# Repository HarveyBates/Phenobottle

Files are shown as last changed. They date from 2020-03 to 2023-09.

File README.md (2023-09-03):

Phenobottle

Phenobottle

---

### Description

An open-source Raspberry-Pi based photobioreactor for cultivating and assessing physiology (photosynthesis & productivity) in microscopic algae. The device can be used to cultivate both green algae and cyanobacteria while continuiously (and non-invasively) probing photosynthetic and growth phenotypes.

#### Publication

The device was published in [Algal Research in 2020](https://www.sciencedirect.com/science/article/abs/pii/S2211926420309735):

*The Phenobottle, an open-source photobioreactor platform for environmental simulation - Bates et al. 2020*



#### Future of The Phenobottle

The Phenobottle is currently being updated to version 0.2. This will feature several environmental controls that were not featured the original version (v0.1) of the device. Additonal environmental sensors will also feature in version 0.2 along with a graphical user interface (GUI). 

If you would like to learn more about the progress of this version please email: [harvey_bates@hotmail.com](harvey_bates@hotmail.com)

---

### [Live](https://youtu.be/7FyAfFrLizw) Preview

PhenobottleGIF (https://youtu.be/7FyAfFrLizw)

___

# Operating Manual

## Specifications

| Feature                                                      | Value / Description                                          |
| ------------------------------------------------------------ | ------------------------------------------------------------ |
| Growth light quality                                         | Red, green and blue (Adjustable). 8-bit individual adjustment for each channel. |
| Growth light intensity                                       | Up to 200 &mu;E (can be increased if needed).                |
| Mixing                                                       | Vertical mixing using magnetic stirrer (adjustable intensity) |
| Bubbling                                                     | Included bubbling motor (adjustable) or solenoid control for external supply of CO<sub>2</sub> |
| Main board                                                   | Raspberry Pi 3B+ (can accomidate the new 4 - 4B)             |
| Microcontroller                                              | Teensy 3.5/3.6 or Teensy 4.1 (3.6 Recommended)               |
| Actinic LED colors                                           | **Blue** 455 – 485 nm (466 nm), **Green** 517 – 555 nm (532 nm), **Orange** 583 – 600 nm (593 nm), **Red** 617 – 635 nm (626 nm). |
| Resolution of **optical density** and **chlorophyll fluorescence** measurments | 10 to 16-bit (adjustable)                                    |
| Sampling rate of fluorometer                                 | 8 &mu;s at 12-bits (can be overclocked)                      |
| Operating voltage                                            | 15 V 1.2 A (Barrel plug), 12 V 2 A (Barrel Plug) and a 5 V 2 A (MicroUSB) power supply |
| Data collection                                              | SQL Server and local .csv                                    |

## Downloading files from this repository

As the Phenobottle is being updated constantly, please download a released version of the device from the releases tab (located on the right hand side of the screen). This contains all the files needed to 3D-print and control Phenobottles as well as some information about the required materials and tools. 

If you wish to clone the main repository you may; however, as there are new versions of the Phenobottle in the works, the files may not work as planned.

## Python dependencies

A number of packages are included in the [Phenobottle_RaspberryPi.py](Phenobottle_RaspberryPi.py). Some of which are already installed on a Raspberry Pi and as such wont be discussed. Others need to be installed using the Raspberry Pi terminal before compiling, these include: 
### PyMySQL - For SQL connection
#### Terminal
```bash
pip3 install PyMySQL
```
#### Python
```python
import pymysql.cursors
```
This requires a Raspberry Pi to be configured as a dedicated SQL server. Information on how to do that can be found [here](https://pimylifeup.com/raspberry-pi-mysql/). It is recomended that you use a dedicated Raspberry Pi for the SQL server; however, you can use one of the Phenobottle's Raspberry Pi's as a server if you are limited.

### Adafruit_MotorHAT - For I2C communication with the [Adafruit-MotorHAT](https://www.adafruit.com/product/2348)
#### Terminal
```bash
git clone https://github.com/adafruit/Adafruit-Motor-HAT-Python-Library.git
cd Adafruit-Motor-HAT-Python-Library
python3 setup.py install
```
#### Python
```python
from Adafruit_MotorHAT import Adafruit_MotorHAT
```
Unfortunatly this package is depreciated; however, its still fine to use for the Phenobottle.

### Twilio - SMS messaging
#### Terminal
```bash
pip3 install twilio
```
#### Python
```python
from twilio.rest import Client
```
This package is not required if you do not want to recieve SMS updates. Twilio is a paid service that you must sign up for [here](https://www.twilio.com/). However, this is non-essential and the Phenobottle runs fine without this addition. This can be handy if you are away from The Phenobottle and need to know how the experiment is running. 

### pySerial - Serial (USB) communication with the microcontroller
#### Terminal
```bash
python3 -m pip install pyserial
```
#### Python
```python
import serial
```
Required for communication with the Teensy 3.6 microcontroller. Documentation on this package can be found [here](https://pyserial.readthedocs.io/en/latest/index.html). 

## Required setup in [Phenobottle_RaspberryPi.py](Phenobottle_RaspberryPi.py)
### Basic Setup
```python
PHENOBOTTLE_NUMBER = 3 # Arbitary number to differentiate between Phenobottles
INITIAL_OPTICAL_DENSITY = 888 # 12-bit value obtained by calibrating the optical density sensor
ARDUINO_FLUORESCENCE_REFERENCE = 3.3 # Teensy microntrollers have 2 analog reference values 1.1 and 3.3 
MIXING_SPEED = 32 # Mixing speed of the mixing motor (0 - 255)
BUBBLING_INTENSITY = 60 # Bubbling intensity of the bubbling motor (0 - 255)
LIGHT_INTENSITY = 220 # Overall light intensity of the grow lights (0 - 255) 
PERISTALTIC_SPEED = 160 # Speed of the peristaltic pump (0 - 255)
EXPERIMENT_START_TIME = "07:00:00" # Specify when the experiment should start 

ser = serial.Serial('/dev/ttyACM0', 115200) # Serial port and baud rate of Teensy 3.6 microcontroller
```
The `INITAL_OPTICAL_DENSITY` value is obtained by reading the raw value of optical density BEFORE adding microalgae to the flask. This can be acheived by writing "MeasureOpticalDensity" in the serial input of the Teensy 3.6 microcontroller (in the ArduinoIDE) or calling `Test.prelim_od()` in the python [file](Phenobottle_RaspberryPi.py). This is required to obtain a 100% transmission reading for which optical density measurments can be formulated from in the code. 

### SQL Setup
```python
connection = pymysql.connect(host='IP_ADDRESS', # IP address of Raspberry Pi SQL server
                             port=port_number, # Usually 3306
                             user='Username', # Username of phpmyadmin 
                             password='Password', # Password of phpmyadmin
                             db='Phenobottle No.%s' %PHENOBOTTLE_NUMBER, # Database name
                             charset='utf8mb4',
                             cursorclass=pymysql.cursors.DictCursor)
```
For a SQL server connection this command must be compiled. See [here](https://pypi.org/project/PyMySQL/) for some documentation related to PyMySQL. For the database name you can change this to whichever name you choose; however, here we have premaded databases in out SQL server named "Phenobottle No.1", "Phenobottle No.2" ..., so that the `PHENOBOTTLE_NUMBER` corresponds with the correct database. 

### Messaging Setup
```python
acc_sid = "Account SSID" # Accound SSID from Twilio
auth_token = "Account Token" # Accound token from Twilio
client = Client(acc_sid, auth_token)
from_number = "Twilio Phone Number" # Designated twilio phone number
to_number = "Mobile Phone Number" # Your phone number
```
As mentioned above, this part isn't really nessessary. However, information regarding the setup of SMS messaging can be found [here](https://www.twilio.com/).

## Experimental procedure
### Measurment Intervals
The Phenobottle is capable of measuring/controling environmental variables at described intervals. This is done through this set of commands:
```python
""" Here we can check if the current time in minutes is devisable by our required measuring interval in this case 10 minutes. This means every 10 minutes a routine (day or night) will be run."""
if datetime.datetime.now().minute % 10 == 0: 
    """ Here we can setup or morning (8:00) and night times (20:00)"""
    if Experiment.experiment_schedule(datetime.time(8, 00), datetime.time(20, 00)): 
        NOW = datetime.datetime.now()
        Experiment.day_routine() # Runs the day routine
    else:
        NOW = datetime.datetime.now() 
        Experiment.night_routine() # Runs the night routine
```
### Routines
The day and the night routine are idential except for the fact that during the night the LED grow lights are constantly switched OFF. 
```python
MotorsAndLights.light_on(None) # Turn on lights (daytime only) with desired color
MotorsAndLights.mixing_motor_on() # Mixing on at set speed
time.sleep(30) # Wait 30 seconds for mixing 

MotorsAndLights.mixing_motor_off() # Mixing off
MotorsAndLights.light_off() # Lights off to ensure no noise from PWM interferes with measurments
Sensors.measure_optical_density() # Measures optical density
Sensors.measure_fluorescence() # Measures fluorescence

MotorsAndLights.light_on(None) # Turn on lights (daytime only) with desired color
MotorsAndLights.peristaltic_motor_on() # Pump on to clear cuvette
Database.upload() # Upload to SQL server
Excel.upload() # Upload to local .csv file
time.sleep(20) # Wait for pump to clear cuvette 

MotorsAndLights.peristaltic_motor_off() # Stop pump
MotorsAndLights.bubbling_motor_on() # Bubble main culture flask on
MotorsAndLights.mixing_motor_on() # Mixing on to homogenate culture
time.sleep(30) # Wait 30 seconds for bubbling and mixing 

MotorsAndLights.bubbling_motor_off() # Bubbling off
MotorsAndLights.mixing_motor_off() # Mixing off
```
This procedure is completely customisable, i.e. methods can be swapped around and the length of certain processes such as the bubbling time can be increased easily. 

# [Teensy 3.6](https://www.pjrc.com/store/teensy36.html) Microcontroller 
Analog functions are carried out by a Teensy 3.6 microcontroller which is connected to the Rasberry Pi via a serial (USB) connection. These analog functions include the measurement of optical density (growth), temperture and chlorophyll fluorescence (photosynthesis). 

The Teensy microcontroller can be programed with the [Arduino IDE](https://www.arduino.cc/en/Main/Software) on the Raspberry Pi if the additional software provided by [PJRC](https://www.pjrc.com/) called [Teensyduino](https://www.pjrc.com/teensy/teensyduino.html) is installed. 

The Teensy [code](Phenobottle_Teensy.ino) is flashed to the Teensy board and doesn't need modifying as it acts as a slave to the Raspberry Pi. 

## Teensy Setup
```c++
void setup() {
  Serial.begin(115200); // Initalise serial communications at specific baud rate
  analogReadResolution(12); // Set the resolution of the microcontroller in bits
  set_reference_voltage(refVoltage); // Only applicable with a Teensy 3.6 (disable if using other microcontroller)
  ...
}
```
## Teensy Slave Setup
The Teensy is constantly checking if there is requests in its serial port from the Raspberry Pi. It does this via the main loop:
```c++
void loop(){
  if(Serial.available()){   
    command = Serial.readStringUntil('\n');
    if(command.equals("MeasureOpticalDensity") || command.equals("MOD")){
      measure_optical_density();
    }
    else if(command.equals("MeasureFluorescence") || command.equals("MF")){
      measure_fluorescence();
    }
    ...
}
```
For example, when a string containing ```"MeasureOpticalDensity"``` into the Teensy's serial port, the resulting function ```measure_optical_density()``` is carried out. This simple design makes it easy to add new requests from the Raspberry Pi [.py](Phenobottle_RaspberryPi.py) file and the Teensy [.ino](Phenobottle_Teensy.ino) file by adding a new `else if` statement to this loop. 

## Fluorescence Measurment
### Setup
The Teensy in its current configuration takes a one second measurement of chlorophyll fluorescence, this however, can be adjusted as described below. The first part is to create arrays of different sizes corresponding to the time between measurements of fluorescence. The one second measurement is comprised of over 2000 data points which are comprised of fast (microsecond timescales) and slow (millisecond timescales) measurments:
2. Micro - Comprised of microsecond measurments (~8 &mu;s between measurments) of a set amount
3. Milli - Comprised of millisecond measurements (~1 ms between measurements) of a set amount
```c++
// Setup arrays that hold fluorescence data
int microRead [1000];
int milliRead[1000];

// Setup arrays that hold timestamps that correspond to fluorescence values
float microTime[1000]; 
float milliTime[1000];
String command;

int microLength = 1000, milliLength = 1000; // Change these to match the size of the above arrays
```
### Read
The measurment procedure is as follows:
```c++
void measure_fluorescence() {
  set_reference_voltage(refVoltage); 
  digitalWrite(actinicPin, HIGH); // Turn on actinic LED
  long timer = micros(); // Start timer 
  ...
```
The measurment is carried out in two seperate parts (1) `microRead` and (2) `milliRead`. The `analogRead` values are stored in their respective arrays with corresponding timestamps in their own array.
```c++
  // Read microsecond fluorescence values and corresponding timestamps
  for (unsigned int i = 0; i < sizeof(microRead) / sizeof(int); i++) 
  {
    microRead[i] = analogRead(fluorescenceReadPin);
    microTime[i] = micros() - timer;
  }

  // Read millisecond fluorescence values and corresponding timestamps
  for (unsigned int i = 0; i < sizeof(milliRead) / sizeof(int); i++) 
  {
    milliRead[i] = analogRead(fluorescenceReadPin);
    milliTime[i] = micros() - timer;
    delay(1); // Delay ~ 1ms between aqusisitions
  }
  ...
```
Any processing (converting timestamps from `micros` to milliseconds) of the arrays after this measurment is carried out after the actinic LED is switched off. This speeds up the `analogRead` function as we only need to store array values while measuring. 

## Optical Density
Measurment of optical density is really simple. 
```c++
void measure_optical_density(){
  set_reference_voltage(refVoltage);
  digitalWrite(odEmitPin, HIGH); // Turn on emitting LED
  delay(500); // Slight delay to ensure emitting LED is stable
  int odMeasure = analogRead(odReadPin); // Read optical density
  Serial.println(odMeasure);
  digitalWrite(odEmitPin, LOW); // Turn off emitting LED
}
```

# Open-Source Licensing

The software in this work is licensed under GNU AFFERO GENERAL PUBLIC LICENSE
  Copyright (C) (2020)  (Harvey Bates)

  This program is free software: you can redistribute it and/or modify
  it under the terms of the GNU General Public License as published by
  the Free Software Foundation, either version 3 of the License, or
  (at your option) any later version.

  This program is distributed in the hope that it will be useful,
  but WITHOUT ANY WARRANTY; without even the implied warranty of
  MERCHANTABILITY or FITNESS FOR A PARTICULAR PURPOSE.  See the
  GNU General Public License for more details.

  You should have received a copy of the GNU General Public License
  along with this program.  If not, see <https://www.gnu.org/licenses/>

  For more information contact: harvey.bates@student.uts.edu.au



Hardware (3D Models, Electronic Schematics) in this work is licensed under a <a rel="license" href="http://creativecommons.org/licenses/by-sa/3.0/">Creative Commons Attribution-ShareAlike 3.0 Unported License</a>.

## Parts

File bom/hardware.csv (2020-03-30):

Item | Quantity | Supplier | Notes
Mainframe | 1 | 3D Print
Lid | 1 | 3D Print
Magnetic Motor Attachment | 1 | 3D Print
Culture Flask Cap | 1 | 3D Print
Circuit Board | 1 | JLCPCB or Other | Upload "Phenobottle_Circuit_Gerber" to JLCPCB
Mixing Motor | 1 | YM2716, Jaycar, Rydalmere, AUS
Bubbling Motor | 1 | Vacuum Pump 12V, Core-Electronics, Kotara, AUS
Peristaltic Motor | 1 | 50220, Makeblock, Shenzhen, China
Light Strips | ~50 cm | RGB LED Bare, Core-Electronics, Kotara, AUS
Raspberry Pi 3B+ | 1
Raspberry Pi Motor HAT | 1 | Adafruit
Teensy 3.6 | 1
Stacking Headers (8 Pin) | 12 | Dfrobot | To connect teensy to circuit board
USB to Micro-USB cable | 1 |  | To connect teensy to rpi. Shorter the better.
875 nm LED | 2 | SIR333-A, Everlight, New Taipei City, Taiwan
10 W LED (COB SMD Chip) | 1 | Ebay | 466 nm, 532 nm, 592 nm, 626 nm
Heat Sink for LED (Optional) | 1 |  | 20 mm x 20 mm
Wire (Red and Black) | 25 m | 0.12 mm guage | For connecting motors to Motor HAT
Silicone Tubing | 5 m | 310-0305, Gecko Optical, Joondalup, AUS5 | 5mm OD x 3 ID mm. Use this to connect all tubing and inside of peristaltic pump. Use Irrigation Joiners (see below)
Polystrene Spectrometer Cuvette | 1 | C5291, Sigma Aldrich, NSW, AUS | Cut the bottom off
Poly Irrigation Barbed 4mm Joiner T/off Pk10 | 1 | Pope | Stick these to bottom and top of poly cuvette
Selleys aquafix glue (Epoxy) | 1 | Selleys | Use this to glue the above (or a waterproof alternative
Selleys 5 minute (Epoxy) ultraclear | 1 | Selleys | Use this to glue other parts (LEDs, motor attachments etc.)
12 V 2 A power supply | 1 | 15DYS624, Ideal Power, Texas, AUS | To power motors through motor hat
DC barrel jack adaptor (Female) | 1 | Dfrobot | Use this to attach the 12v 2a power supply to the motor hat
15 V 1.2 A power supply | 1 | DYS618 | Plug this into the phenobottle circuit board dc plug
5 V 2.5 A power supply | 1 | Raspberry Pi | Use this to power the raspberry pi
695 nm longpass filter | 1 | Thorlabs, New Jersey, USA | For fluorometer (position infront of photodiode)
IR cut-off filter | 1 | IR Filter, Lilly Electronics, Q-BAIHE, Hubei Province, ROC | For fluorometer (position infront of emitting LED)
Falcon Flask (Culture Flask) | 1 | Falcon Flask, Corning, NY, USA
Nylon 5/32" OD | 30 | Any | Glued inside cap to attach silicone tubing to
Neudynium Magnets | 2 | Any | 5 mm OD x 2 mm W

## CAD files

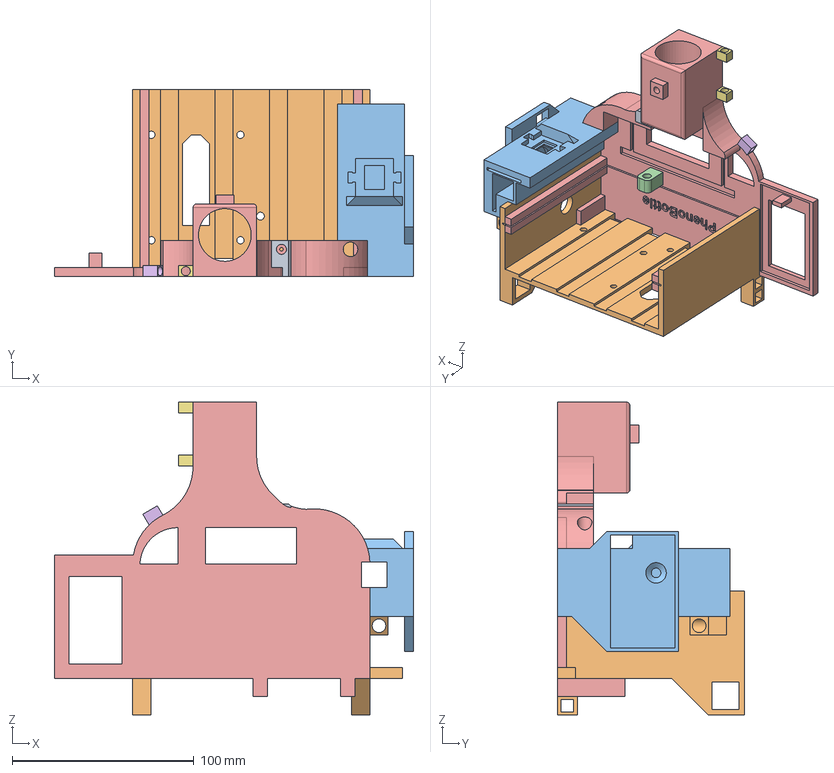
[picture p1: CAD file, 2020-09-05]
models/STEP Files/Phenobottle Main Frame.step
197.5 x 103.0 x 172.0 mm
OD Emitter Module
Light Enclosure
FluroHolder
OD Detector Module

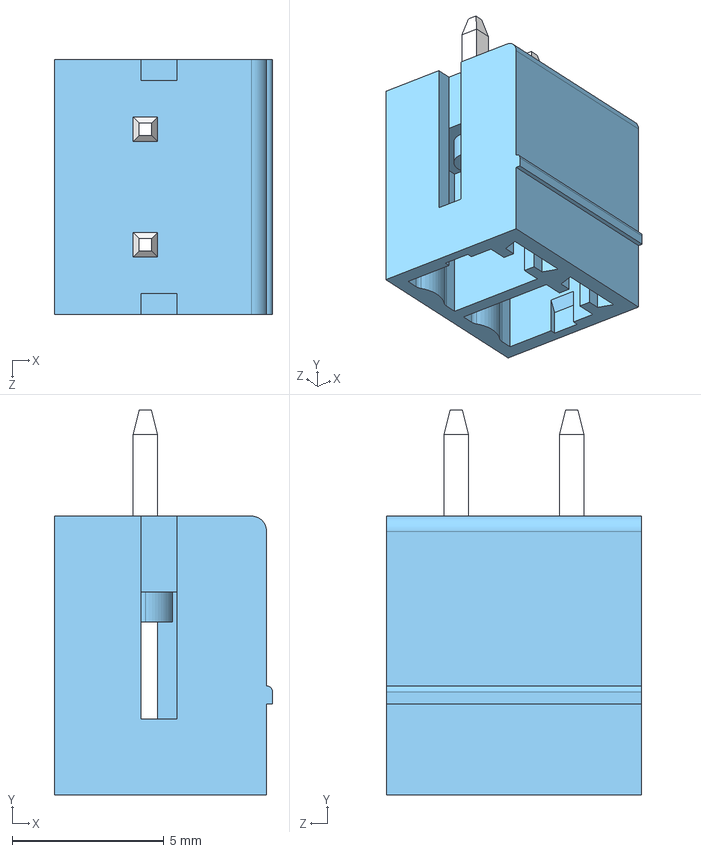
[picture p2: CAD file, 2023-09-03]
electronics/phenobottle/components/extern/3dmodels/connectors/TBP02R2-381-02BE.step
7.20 x 12.7 x 8.41 mm

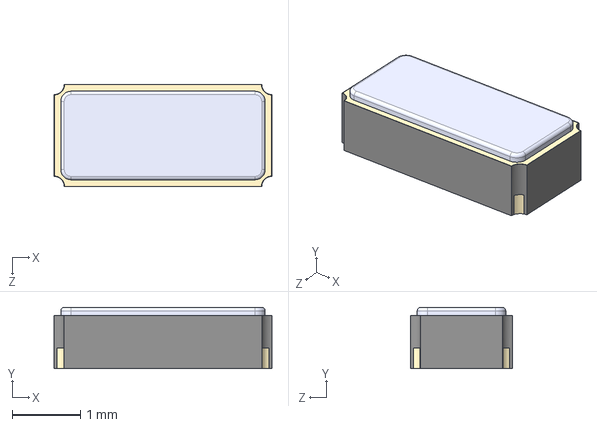
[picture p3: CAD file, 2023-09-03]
electronics/phenobottle/components/extern/3dmodels/crystals/ECS-.327-12.5-34R-C-TR.step
3.20 x 0.9 x 1.50 mm

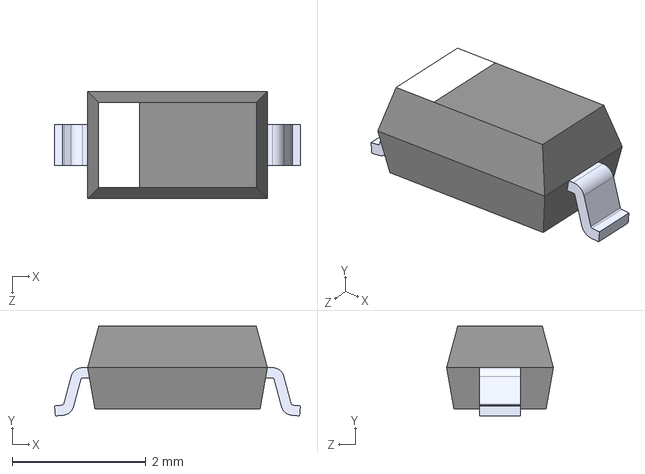
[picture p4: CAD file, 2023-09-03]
electronics/phenobottle/components/extern/3dmodels/diodes/MMSZ4700T1G.step
3.68 x 1.35 x 1.60 mm

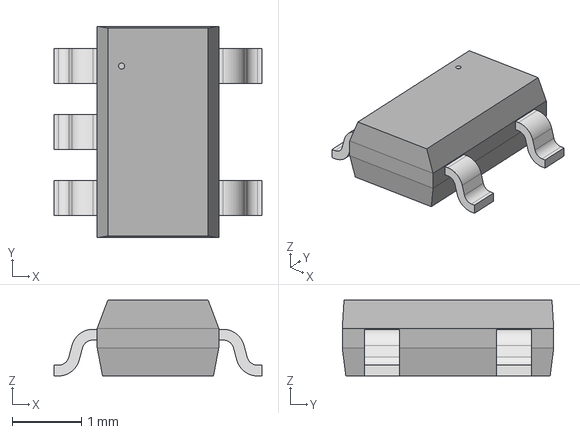
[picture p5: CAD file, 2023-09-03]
electronics/phenobottle/components/extern/3dmodels/op_amps/OPA328DBVR.step
3.00 x 3.05 x 1.09 mm

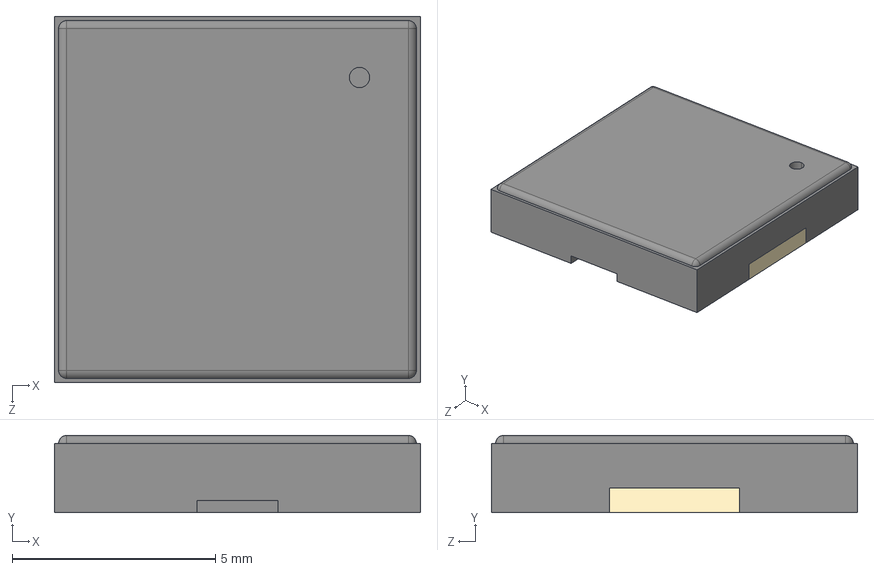
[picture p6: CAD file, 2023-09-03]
electronics/phenobottle/components/extern/3dmodels/piezo/PKMCS0909E4000-R1.step
9.00 x 1.90 x 9.00 mm

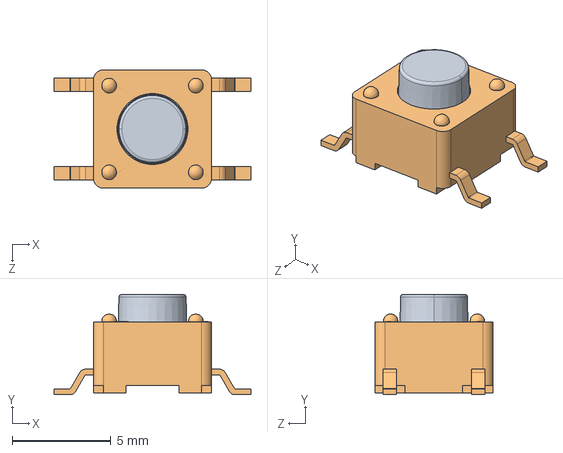
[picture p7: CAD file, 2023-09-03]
electronics/phenobottle/components/extern/3dmodels/switch_tactile/TL3301AF160QG.step
10.0 x 5.10 x 6.00 mm

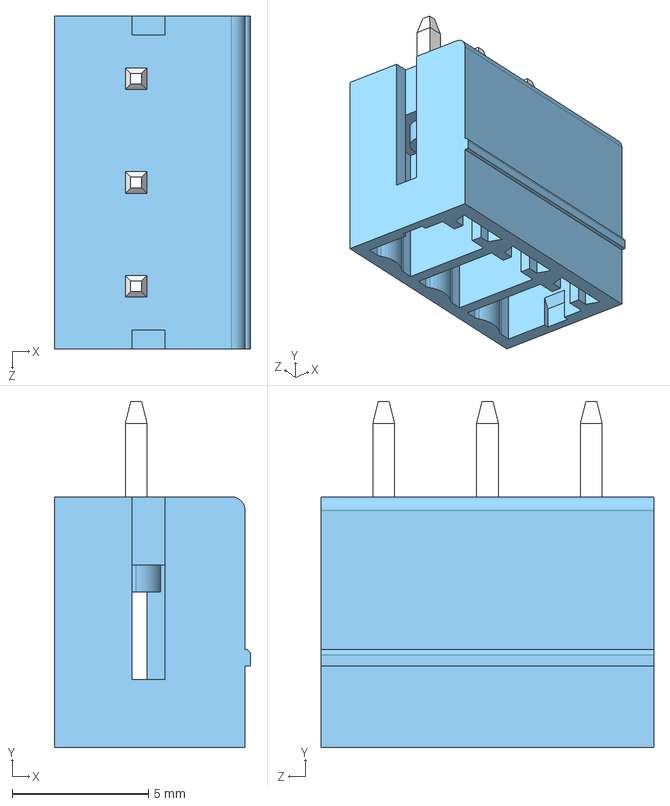
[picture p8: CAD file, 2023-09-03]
electronics/phenobottle/components/extern/3dmodels/connectors/TBP02R2-381-03BE.step
7.20 x 12.7 x 12.2 mm

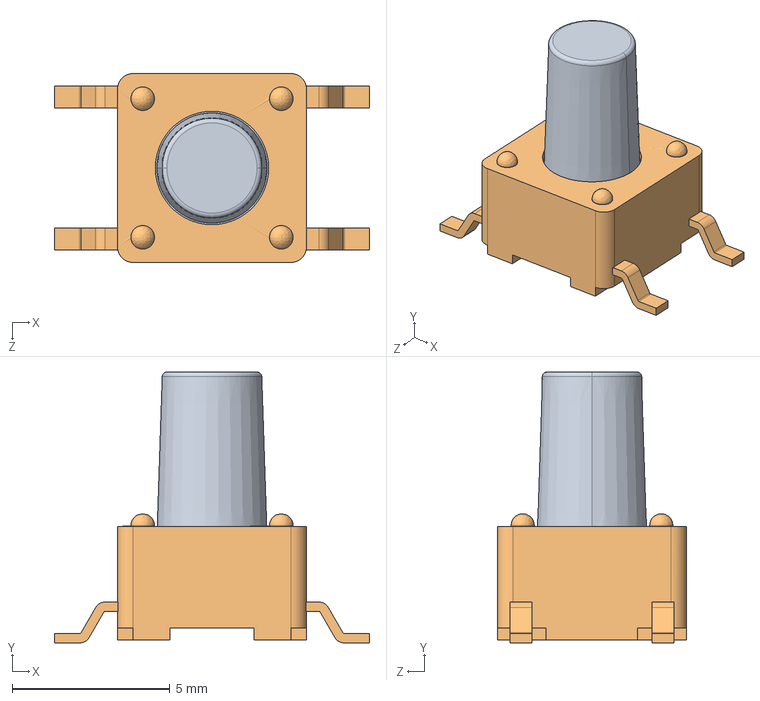
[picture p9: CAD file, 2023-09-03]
electronics/phenobottle/components/extern/3dmodels/switch_tactile/TL3301PF160QG.STEP
10.0 x 8.60 x 6.00 mm

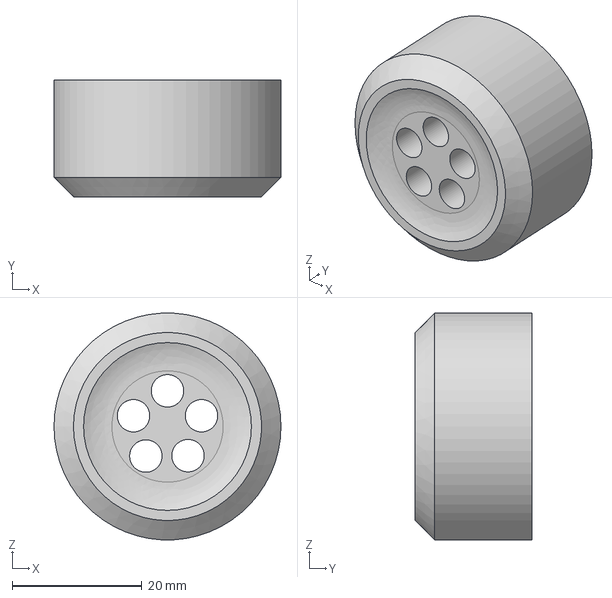
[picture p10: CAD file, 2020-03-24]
models/STEP Files/Phenobottle Culture Flask Cap.step
35.0 x 18.0 x 34.9 mm

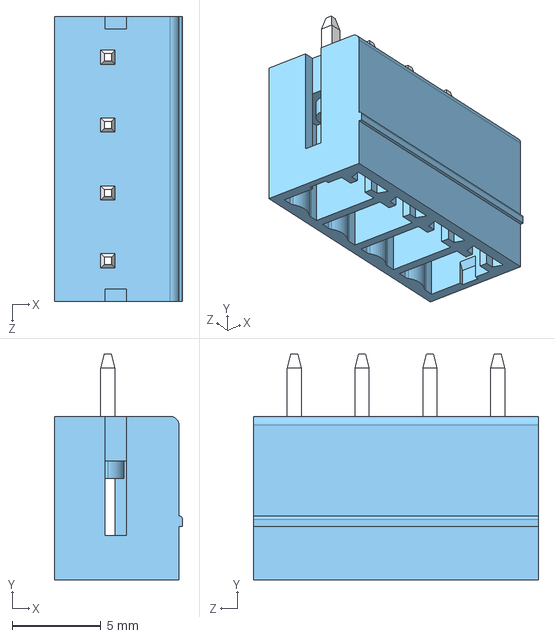
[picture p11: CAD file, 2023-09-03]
electronics/phenobottle/components/extern/3dmodels/connectors/TBP02R2-381-04BE.step
7.20 x 12.7 x 16.0 mm

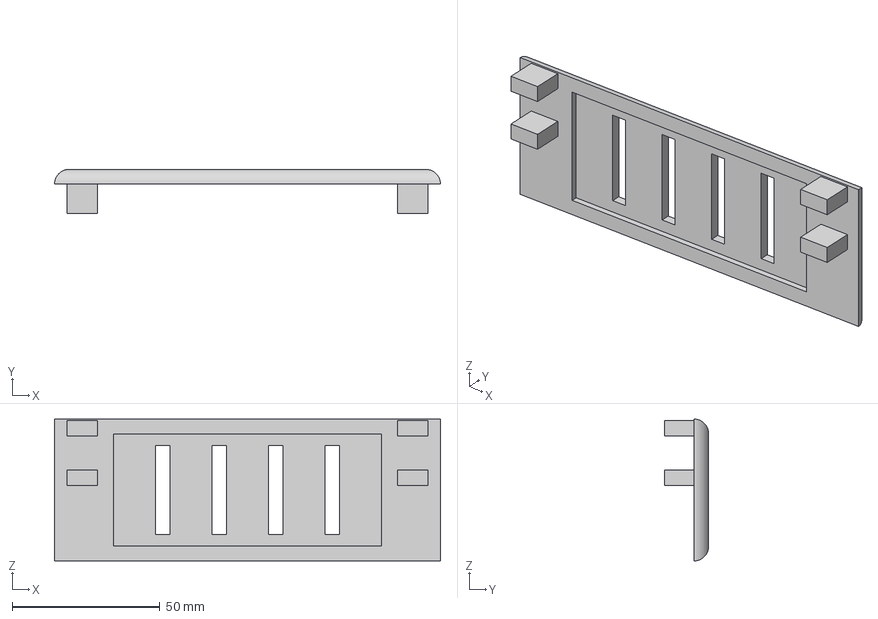
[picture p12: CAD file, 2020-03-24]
models/STEP Files/Phenobottle Lid.step
130.5 x 15.0 x 48.0 mm

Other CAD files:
electronics/phenobottle/components/extern/3dmodels/fuses/0154010.DRL.step
electronics/phenobottle/components/extern/3dmodels/ldo/AP63205WU-7.step
electronics/phenobottle/components/extern/3dmodels/ldo/MIC29150-12WU.step
electronics/phenobottle/components/extern/3dmodels/ldo/MIC29300-5.0WU-TR.step
models/STEP Files/Phenobottle Magnetic Motor Attachment.step
models/STL Files/Phenobottle Culture Flask Cap.stl
models/STL Files/Phenobottle Lid.stl
models/STL Files/Phenobottle Magnetic Motor Attachment.stl
models/STL Files/Phenobottle Main Frame.stl

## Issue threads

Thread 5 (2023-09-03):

### ISSUE TITLE
Subscribe to topics on first startup

### ISSUE THREAD

**Issue by HarveyBates** [HarveyBates/Phenobottle#5]
Need to subscribe to all basic MQTT topics on setup. The best way to do this (I think) is by using a shell script as I can start by:

1. Installing dependancies (mosquitto etc.)
2. Creating unique user id (16 digit random number letter sequence) and adding user credentials to MQTT-Broker / Database
3. Subscribe the current user to all basic topics

The topics will be formatted as (baseline list):
{user_id}/{phenobottle_treatment}/sensor/temperature
{user_id}/{phenobottle_treatment}/sensor/optical_density
{user_id}/{phenobottle_treatment}/sensor/fluorescence/parameters
{user_id}/{phenobottle_treatment}/sensor/fluorescence/raw
{user_id}/{phenobottle_treatment}/motor/mixing
{user_id}/{phenobottle_treatment}/motor/media_in
{user_id}/{phenobottle_treatment}/motor/culture_out
{user_id}/{phenobottle_treatment}/lights
{user_id}/{phenobottle_treatment}/temperature/motor
{user_id}/{phenobottle_treatment}/temperature/fan
{user_id}/{phenobottle_treatment}/temperature/peristaltic

*phenobottle_treatment* is defined by the user in JS.

**The issue with this is that the wildcard ```#``` can be used in replacement of {user_id} and/or {phenobottle_treatment} allowing anyone to see the published messages.**

**Comment by CamDavidsonPilon** [comment]
Hey @HarveyBates, I hope you don't mind me jumping in with some comments! Cool to see you using MQTT. I'm still a big fan, but my implementation of it has evolved for Pioreactor, so I can share what I've learned (some of which you may already know):

1. MQTT natively doesn't have timestamps of when messages are created / published, but this is often important for downstream processes (storing in a DB, visualizing on a UI, etc.). I've moved mostly away from sending _floats_ as message payloads, to sending a json string of float-value and timestamps, ex: `{"temperature": 40, "timestamp": "2021-06-21T14:40:36Z"}`. Yes, there is more code, more serializing & unpacking, and more work done by the broker's CPU, but it's worth it. If a connection is lost between client + broker, even for a few seconds, not having a timestamp will create data problems. Also, using a json string allows for other metadata to be passed around.
2. I loosely follow the [Homie convention](https://homieiot.github.io/specification/):
   - their lifecycle section is useful to think about, including variables like`$state` (7.1.2)
   - their `set` topic syntax is nice (7.3.2)
 Keep in mind that the Homie convention is only a guide, and break it (consistently) when you want. 
3. The Python implementation of the client, `paho`, works really well, but has some quirks. For example, you can't publish in a callback. That took me a long time to figure out haha.
4. On the JS side, I found lots of performance improvements when I was able to reuse clients between subscriptions, instead of creating a client for each subscription. 
5. ` mosquitto_sub -v -t "#" -F "%I %t %p"` to show timestamps with the log
6. Almost always, when I've used MQTT as a "database", I've been bitten with a difficult bug / problem later. For example, I keep the state of my LEDs intensity in MQTT, something like `{"A": 50, "B": 0, "C"0}`, and when I update an LED, I subscribe to this topic, unserialize, update json, serialize, and publish back. This sounds fine, but fails down the line: 
   - no guaranteed persistance on disk
   - no way to handle race conditions, eg: multiple ppl trying to update
   - no way to recover if wiped by mistake. 
 
 A proper database does all this, by design. My point is: treat keeping important state _only_ in MQTT as an anti-pattern, i.e. don't turn MQTT into a database. 

Your note: "The issue with this is that the wildcard #..."  is correct, but if the user has the password/username, then they should be _allowed_ to see the entire tree of topics. I think the security should be at the level of username/password - i.e. that pair should only be given to trusted ppl. If multiple parties are using the same broker (the googlable word is "multi-tenant"), you'll need to design the broker to handle that at start up.

**Comment by HarveyBates** [comment]
Hey @CamDavidsonPilon 
Thanks for all the information! Yea it took me a while to come around to MQTT, I recently got a job working on LoRaWAN sensors for agriculture which communicate over MQTT. 

I was checking out your Pioreactor code base this weekend, its clear that you have put in a lot of work, I hope the system is working well for you. Keen for the day I can buy one!

1. That is a really smart idea! Worth it for the timestamps
2. Really good to know about the homie convention, I'm going to have a play around with it this weekend
3. That is good to know, I am tossing up if I should write the client code in C++ but i don't know if it will have the same issue
4. Ok ill look into that some more
5. Thank you!!
6. Yea I think I would have approached it in the same way. In the past when i was using my C++ websockets I formatted my LED packets as strings (**LR&I:50&F:20000**)  which converts to: **Light Color: Red, Intensity: 50 bits, Frequency: 20 kHz**. However, I was counting on my microcontroller to handle that which might be super slow. I'm worried about the race conditions now. Ideally I want the user to either be able to setup an experiment dynamically in JS or just upload a .yaml file if systems fail.
7. haha that would have been rough, I'll keep that in mind

Yea the plan is to have a seperate postgresql database to handle things in regards to data storage. 

I want to manage the MQTT broker for multiple parties so I am going to have to look further into the future. I'll look some more into multi tenants! 

Thank you!

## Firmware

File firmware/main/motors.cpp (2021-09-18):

#include "motors.h"

Motors::Motors(){
  pinMode(mixingIN1, OUTPUT);
  pinMode(mixingIN2, OUTPUT);
  
  pinMode(fanIN1, OUTPUT);
  pinMode(fanIN2, OUTPUT);
  
  pinMode(pumpIN1, OUTPUT);
  pinMode(pumpIN2, OUTPUT);
}


void Motors::on(const char* type){
  /**
   * Turn on specific type of motor at a preset intensity and frequency. 
   * @param type Type of motor.
   */
  if(strcmp(type, "Mixing") == 0){
    analogWriteFrequency(mixingIN1, mixingFrequency);
    analogWriteFrequency(mixingIN2, mixingFrequency);
    digitalWrite(mixingIN2, LOW);
    analogWrite(mixingIN1, mixingIntensity);
  }
  else if(strcmp(type, "Fan") == 0){
    analogWriteFrequency(fanIN1, fanFrequency);
    analogWriteFrequency(fanIN2, fanFrequency);
    digitalWrite(fanIN2, LOW);
    analogWrite(fanIN1, fanIntensity);
  }
  else if(strcmp(type, "Pump") == 0){
    analogWriteFrequency(pumpIN1, pumpFrequency);
    analogWriteFrequency(pumpIN2, pumpFrequency);
    digitalWrite(pumpIN2, LOW);
    analogWrite(pumpIN1, pumpIntensity);
  }
}

void Motors::on(const char* type, int intensity){
  /**
   * Turn on specific motor with custom intensity and a preset frequency.
   * @param type Type of motor.
   * @param intensity Intensity (in Bits) of PWM.
   */
  if(strcmp(type, "Mixing") == 0){
    mixingIntensity = intensity;
    analogWriteFrequency(mixingIN1, mixingFrequency);
    analogWriteFrequency(mixingIN2, mixingFrequency);
    digitalWrite(mixingIN2, LOW);
    analogWrite(mixingIN1, mixingIntensity);
  }
  else if(strcmp(type, "Fan") == 0){
    fanIntensity = intensity;
    analogWriteFrequency(fanIN1, fanFrequency);
    analogWriteFrequency(fanIN2, fanFrequency);
    digitalWrite(fanIN2, LOW);
    analogWrite(fanIN1, fanIntensity);
  }
  else if(strcmp(type, "Pump") == 0){
    pumpIntensity = intensity;
    analogWriteFrequency(pumpIN1, pumpFrequency);
    analogWriteFrequency(pumpIN2, pumpFrequency);
    digitalWrite(pumpIN2, LOW);
    analogWrite(pumpIN1, pumpIntensity);
  }
}


void Motors::set_frequency(const char* type, int freq){
  /**
   * Set the freqeuency (in Hz) of a specific motor.
   * 
   * This requires initalising this change by running on()
   * 
   * @param type Type of motor.
   * @param freq Frequency (in Hz) of the PWM emission.
   */
  if(strcmp(type, "Mixing") == 0){
    mixingFrequency = freq;
  }
  else if(strcmp(type, "Fan") == 0){
    fanFrequency = freq;
  }
  else if(strcmp(type, "Pump") == 0){
    pumpFrequency = freq;
  }
}


void Motors::set_intensity(const char* type, int intensity){
  /**
   * Set the intensity (in Bits) of a specific motor.
   * 
   * This requires initalising this change by running on()
   * 
   * @param type Type of motor.
   * @param intensity Intensity (in Bits) of the PWM LED emission.
   * 
   * @todo convert this to percentage
   */
  if(strcmp(type, "Mixing") == 0){
    mixingIntensity = intensity;
  }
  else if(strcmp(type, "Fan") == 0){
    fanIntensity = intensity;
  }
  else if(strcmp(type, "Pump") == 0){
    pumpIntensity = intensity;
  }
}



void Motors::off(){
  /**
   * Turn off all Motors and reset intensity to zero.
   */
  mixingIntensity = 0;
  
  digitalWrite(mixingIN2, LOW);
  analogWrite(mixingIN1, mixingIntensity);

  digitalWrite(fanIN2, LOW);
  analogWrite(fanIN1, fanIntensity);

  digitalWrite(pumpIN2, LOW);
  analogWrite(pumpIN1, pumpIntensity);
}


void Motors::off(const char* type){
  /**
   * Turn off specific motor.
   * 
   * @param type Type of motor.
   */
  if(strcmp(type, "Mixing") == 0){
    mixingIntensity = 0;
  }
  else if(strcmp(type, "Fan") == 0){
    fanIntensity = 0;
  }
  else if(strcmp(type, "Pump") == 0){
    pumpIntensity = 0;
  }
}

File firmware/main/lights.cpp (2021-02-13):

#include "lights.h"

Lights::Lights(){
  /**
   * Initalise microcontroller pins as outputs upon startup.
   */
  pinMode(redIN1, OUTPUT);
  pinMode(redIN2, OUTPUT);
  pinMode(greenIN1, OUTPUT);
  pinMode(greenIN2, OUTPUT);
  pinMode(blueIN1, OUTPUT);
  pinMode(blueIN2, OUTPUT);
}

void Lights::on(const char* color){
  /**
   * Turn on specific color of light at a preset intensity and frequency. 
   * @param color Color of the LED.
   */
  if(strcmp(color, "Red") == 0){
    analogWriteFrequency(redIN1, redFrequency);
    analogWriteFrequency(redIN2, redFrequency);
    digitalWrite(redIN2, LOW);
    analogWrite(redIN1, redIntensity);
  }
  else if(strcmp(color, "Green") == 0){
    analogWriteFrequency(greenIN1, greenFrequency);
    analogWriteFrequency(greenIN2, greenFrequency);
    digitalWrite(greenIN2, LOW);
    analogWrite(greenIN1, greenIntensity);
  }
  else if(strcmp(color, "Blue") == 0){
    analogWriteFrequency(blueIN1, blueFrequency);
    analogWriteFrequency(blueIN2, blueFrequency);
    digitalWrite(blueIN2, LOW);
    analogWrite(blueIN1, blueIntensity);
  }
}

void Lights::on(const char* color, int intensity){
  /**
   * Turn on specific color of light with custom intensity and a preset frequency.
   * @param color Color of the LED.
   * @param intensity Intensity (in Bits) of the PWM LED emission.
   */
  if(strcmp(color, "Red") == 0){
    redIntensity = intensity;
    analogWriteFrequency(redIN1, redFrequency);
    analogWriteFrequency(redIN2, redFrequency);
    digitalWrite(redIN2, LOW);
    analogWrite(redIN1, redIntensity);
  }
  else if(strcmp(color, "Green") == 0){
    greenIntensity = intensity;
    analogWriteFrequency(greenIN1, greenFrequency);
    analogWriteFrequency(greenIN2, greenFrequency);
    digitalWrite(greenIN2, LOW);
    analogWrite(greenIN1, greenIntensity);
  }
  else if(strcmp(color, "Blue") == 0){
    blueIntensity = intensity;
    analogWriteFrequency(blueIN1, blueFrequency);
    analogWriteFrequency(blueIN2, blueFrequency);
    digitalWrite(blueIN2, LOW);
    analogWrite(blueIN1, blueIntensity);
  }
}

void Lights::set_frequency(const char* color, int freq){
  /**
   * Set the freqeuency (in Hz) of a specific colors LED emission.
   * 
   * This requires initalising this change by running on()
   * 
   * @param color Color of the LED.
   * @param freq Frequency (in Hz) of the PWM emission.
   */
  if(strcmp(color, "Red") == 0){
    redFrequency = freq;
  }
  else if(strcmp(color, "Green") == 0){
    greenFrequency = freq;
  }
  else if(strcmp(color, "Blue") == 0){
    blueFrequency = freq;
  }
}

void Lights::set_intensity(const char* color, int intensity){
  /**
   * Set the intensity (in Bits) of a specific colors LED emission.
   * 
   * This requires initalising this change by running on()
   * 
   * @param color Color of the LED.
   * @param intensity Intensity (in Bits) of the PWM LED emission.
   * 
   * @todo convert this to percentage
   */
  if(strcmp(color, "Red") == 0){
    redIntensity = intensity;
  }
  else if(strcmp(color, "Green") == 0){
    greenIntensity = intensity;
  }
  else if(strcmp(color, "Blue") == 0){
    blueIntensity = intensity;
  }
}

void Lights::off(){
  /**
   * Turn off all LED's and reset intensity to zero.
   */
  redIntensity = 0;
  greenIntensity = 0;
  blueIntensity = 0;
  
  digitalWrite(redIN2, LOW);
  analogWrite(redIN1, redIntensity);

  digitalWrite(greenIN2, LOW);
  analogWrite(greenIN1, greenIntensity);

  digitalWrite(blueIN2, LOW);
  analogWrite(blueIN1, blueIntensity);

}

void Lights::off(const char* color){
  /**
   * Turn off specific color of LED.
   * 
   * @param color Color of the LED.
   */
  if(strcmp(color, "Red") == 0){
    redIntensity = 0;
  }
  else if(strcmp(color, "Green") == 0){
    greenIntensity = 0;
  }
  else if(strcmp(color, "Blue") == 0){
    blueIntensity = 0;
  }
}

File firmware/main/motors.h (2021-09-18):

#ifndef MOTORS_H
#define MOTORS_H

#include "arduino.h"

// Mixing Pins (Heater 1)
#define mixingIN1 8
#define mixingIN2 9

// Fan Pins (Fan 2)
#define fanIN1 24
#define fanIN2 25
 
// Pump Pins (Heater 2)
#define pumpIN1 10
#define pumpIN2 11

/**
 * Functions that control the intensity and frequency of various motors.
 */
class Motors{
  int16_t mixingIntensity = 0, fanIntensity = 0, pumpIntensity = 0;
  int16_t mixingFrequency = 20000, fanFrequency = 20000, pumpFrequency = 20000;

  public:
    Motors();
    void on(const char* type);
    void on(const char* type, int intensity);
    void set_frequency(const char* type, int freq);
    void set_intensity(const char* type, int intensity);
    void off();
    void off(const char* type);
};


#endif

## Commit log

2020-03-24 Update Phenobottle Raspberry Pi.py
2020-03-24 Rename Phenobottle Raspberry Pi.py to Phenobottle_RaspberryPi.py
2020-03-25 Update Phenobottle Circuit Board BOM.csv
    [Phenobottle Circuit Board BOM.csv]
2020-03-28 Update Phenobottle Hardware BOM.xlsx
    [Phenobottle Hardware BOM.xlsx]
2020-03-30 Fixed Pin Indexing
2020-03-30 Create Phenobottle Hardware BOM.csv
    [Phenobottle Hardware BOM.csv]
2020-09-05 Update Phenobottle Main Frame.step
    Added vent for Raspberry Pi, Teensy 3.6 PCB housing, routing for Mixing Motor
    [Phenobottle Main Frame.step]
2020-10-20 RGB LED Functions
2020-10-20 added raspberry pi information
2020-10-20 added Teensy information
2020-10-20 Update for version 0.1.1
    Updated some of the documentation. Adjusted the Raspberry Pi controls of RGB LED's and added a new circuit for RGB control without extra outputs from the motor HAT.
    [Gerber_BoardOutline.GKO, Gerber_BottomLayer.GBL, Gerber_BottomSolderMaskLayer.GBS, Gerber_Drill_NPTH.DRL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]
2020-11-24 added comments and dynamic way of setting reference voltage
2020-12-06 added data visualizer
    [Gerber_BoardOutline.GKO, Gerber_BottomLayer.GBL, Gerber_BottomSolderMaskLayer.GBS, Gerber_Drill_NPTH.DRL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]
2020-12-28 added teensy motorcontrols
2021-01-29 working on extened msg frame decoding
2021-01-30 frame decoding <125 and 126
2021-01-30 working xor decryption for long and short frames
2021-02-09 added number generation for connected devices
2021-02-13 added temperature cntrl and documentation
2021-02-15 added support for unix devices
2021-03-01 adjusted for cli teensy control
2021-03-07 led array with ir-leds
    [74HC4066D_653.step, 826634-5--3DModel-STEP-1.STEP, AOD417.step, B2B-PH-K-S(LF)(SN)--3DModel-STEP-56544.STEP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]
2021-03-09 led array IR-LED update:
    [282841-5.step, LED Array.kicad_pcb, LED Array.sch, LED Arrayv2.kicad_pcb]
2021-03-10 added led array gerber
    [Gerber_BoardOutline.GKO, Gerber_BottomLayer.GBL, Gerber_BottomSolderMaskLayer.GBS, Gerber_Drill_NPTH.DRL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]
2021-06-20 started python control
    [Phenobottle Circuit Board BOM.csv, Phenobottle Culture Flask Cap.step, Phenobottle Culture Flask Cap.stl, Phenobottle Hardware BOM.csv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]
2021-06-26 working on the site framework
2021-07-06 working on device control
2021-09-18 update for video, heater and motor control
    [1655--3DModel-STEP-56544.STEP, AOD417--3DModel-STEP-56544.STEP, B2B-XH-A(LF)(SN)--3DModel-STEP-56544.STEP, DCJ200-10-A-K1-K--3DModel-STEP-56544.STEP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]
2021-11-22 12 V 3.2 - 3.5 A for the tec controller, heating fast but not cooling
2023-09-03 Update to start next round of testing
    Combining both Open-JIP electronics with Phenobottle electronics to
    consolidate circuit board. Next to add RPi attachment and drivers for
    peltier modules (optional).
    [0154010.DRL.step, 0ZCF0075AF2C.step, 0ZCF0100AF2A.step, 1655--3DModel-STEP-56544.STEP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]
2023-09-03 Added compute module and LED driver
    Need to change 5V regulator for higher current as compute module needs
    around 1 A with no peripherials (perhaps AP63205WU-7).
    [COMPUTE.kicad_sch, flu_excite.kicad_sch, led_driver.kicad_sch, phenobottle.kicad_sch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]
2023-09-04 updated 5V LDO with something that can power a RPi zero and other peripherals
    [AP63205WU-7.step, power.kicad_sch]

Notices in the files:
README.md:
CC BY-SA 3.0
